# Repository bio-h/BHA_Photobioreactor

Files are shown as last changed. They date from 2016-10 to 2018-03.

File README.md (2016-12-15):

#BHA Photobioreactor

This project is still in alpha phase, meaning that the prototype is not functional at all.

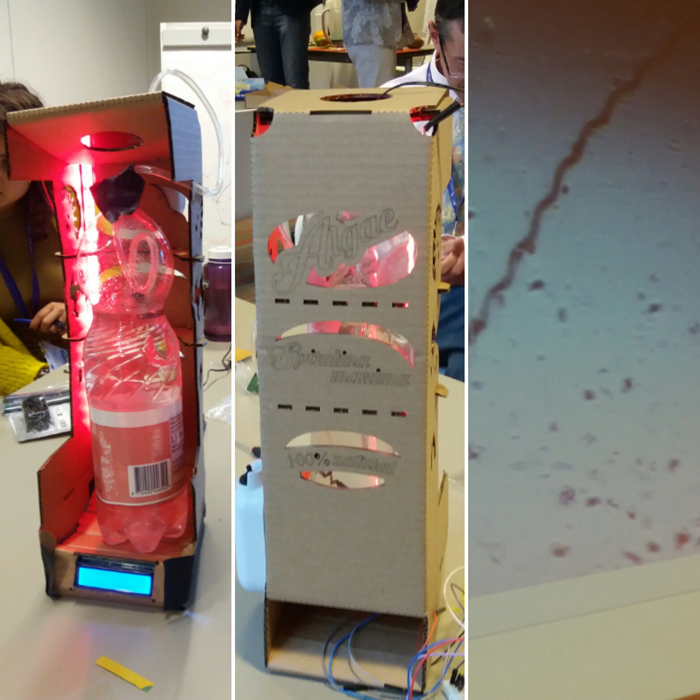
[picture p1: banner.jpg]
DIY Photobioreactor


The first release contains the source files of the designs and materials used during the #FOOD2030EU event in Brussels on Oct 12, 2016. The goal of that workshop was to prototype a device and have a discussion on bottom-up citizens led protein production. We built our own alpha version of the photobioreactor with the aim to grow Spirulina.

The goal of the Photobioreactor is to control or monitor the following parameters:

* Amount of light based on a day / night cycle
* Measure the amount of light
* Measure the pH
* Measure the temperature
* Display these values on an LCD screen

Follow these links for more information on [Spirulina](http://biohackacademy.github.io/bha3/annex/culture-collection/spirulina-maxima/) and its preferred [growth medium](http://biohackacademy.github.io/bha3/annex/cultivation-media/spirulina-medium/).

Here is a [video of a fully completed device](https://www.instagram.com/p/BLeMfMBlUFr/?taken-by=pvanboheemen).

<blockquote class="instagram-media" data-instgrm-captioned data-instgrm-version="7" style=" background:#FFF; border:0; border-radius:3px; box-shadow:0 0 1px 0 rgba(0,0,0,0.5),0 1px 10px 0 rgba(0,0,0,0.15); margin: 1px; max-width:658px; padding:0; width:99.375%; width:-webkit-calc(100% - 2px); width:calc(100% - 2px);"><div style="padding:8px;"> <div style=" background:#F8F8F8; line-height:0; margin-top:40px; padding:50.0% 0; text-align:center; width:100%;"> </div> <p style=" margin:8px 0 0 0; padding:0 4px;"> <a href="https://www.instagram.com/p/BLeMfMBlUFr/" style=" color:#000; font-family:Arial,sans-serif; font-size:14px; font-style:normal; font-weight:normal; line-height:17px; text-decoration:none; word-wrap:break-word;" target="_blank">Done! Spirulina #algea bioreactors build @Food2030EU prototyping how to grow your own protein</a></p> <p style=" color:#c9c8cd; font-family:Arial,sans-serif; font-size:14px; line-height:17px; margin-bottom:0; margin-top:8px; overflow:hidden; padding:8px 0 7px; text-align:center; text-overflow:ellipsis; white-space:nowrap;">A video posted by @pvanboheemen on <time style=" font-family:Arial,sans-serif; font-size:14px; line-height:17px;" datetime="2016-10-12T17:47:55+00:00">Oct 12, 2016 at 10:47am PDT</time></p></div></blockquote> <script async defer src="//platform.instagram.com/en_US/embeds.js"></script>

##Navigation the repo

 	BHA_Photobioreactor/						main repo
 	|-- Arduino/PhotobioreactorController/		Arduino Code
 	|-- Pictures/								Pictures of the device
 	BoM											Bill of Materials
 	Photobioreactor - Breadboard-wiring.png		Wiring overview
 	Photobioreactor - Electronics Assembly Guide.pdf		Assembly guide
 	Photobioreactor - Fritzing.fzz				Wiring source
 	Photobioreactor - Lasercut file.dxf			Laser cut sheet

Special thanks to: #FOOD2030EU @TogetherSci @waag #PolicyLabEU @EU_ScienceHub

## License

All code is licensed under GNU General Public License.

All designs are licensed under Creative Commons Contribution Share-Alike license

Copyright Waag Society

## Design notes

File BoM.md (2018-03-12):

## Bill of Materials

In this design we use the Arduino Leonardo microcontroller. These are abundantly available on the web, for example at [Bens Electronics](https://benselectronics.nl/arduino-leonardo/)(12.00)

### Components

These are the parts you will need to assemble the photobioreactor:

|No|Amount|Description|Supplier NL|Cost|
| ------------: | ------------: | :------------ | :------------ | ------------: |
|1|1|Big sheet of cardboard, just use an old box|-|-|
|2|1|Water proof temperature sensor NTC|[HackerStore](http://www.hackerstore.nl/Artikel/298), [Prototype Shop](http://www.prototypeshop.nl/temperatuursensor-waterdicht-ntc-10k-b3950-met-bevestigingsoog), [Adafruit](https://www.adafruit.com/product/372)|2.95|
|3|1|10K resistor|[Farnell](http://nl.farnell.com/te-connectivity/cfr16j10k/resistor-carbon-10k-0-25w-5/dp/2329474), [EOO](http://www.eoo-bv.nl/index.php?_a=viewProd&productId=7016)|0.06|
|4|1|I2C LCD display|[Bens Electronics](https://benselectronics.nl/16-x-2-hd44780-lcd-+-i2c-adapter-module/), [HackerStore](http://www.hackerstore.nl/Artikel/82), [iPrototype](https://iprototype.nl/products/components/led-lcd/lcd16x2-I2C-BL), [Hackerstore](https://www.hackerstore.nl/Artikel/82)|5.95|
|5|1|Digital Lux sensor (*1)|[HobbyElectronica](https://www.hobbyelectronica.nl/product/tsl2561-digitale-lux-licht-sensor/)|7.95|
|6|1|Digital lux sensor (*1)|[Bens Electronics](https://benselectronics.nl/gy302-bh1750-licht-intensiteit-sensor/)|3.50|
|7|1|Backflow valve|[Vijverbenodigdheden](https://www.vijverbenodigdheden.nl/tussenklep-terugslagklep-4-mm)|0.75|
|8|1|pH sensor|[iPrototype](https://www.iprototype.nl/products/components/sensors/analog-ph-meter-kit)|33.95|
|9|1|Relay|[Hobby Electronica](https://www.hobbyelectronica.nl/product/relais-module-2-kanaals-5v/)|2.95|
|10|1|Breadboard|[Bens Electronics](https://benselectronics.nl/breadboard-400-points/), [HackerStore](http://www.hackerstore.nl/Artikel/50)|3.00|
|11|2|Jumpwires|[Bens Electronics](https://benselectronics.nl/dupont-20cm-male-male/), [HackerStore](http://www.hackerstore.nl/Artikel/472)|0.75|
|12|2|Male-female wires|[Bens Electronics](https://benselectronics.nl/dupont-20cm-male-female/), [HackerStore](http://www.hackerstore.nl/Artikel/222)|0.75|
|13|1|Air pump|[Raven Hengelsport](https://www.raven.nl/raven-luchtpomp/nl/product/43517/)|8.99|
|14|1|Battery Alkaline C|[Albert Heijn](http://www.ah.nl/producten/product/wi136833/ah-alkaline-c-batterijen)|1.00|
|15|1|LED strip|[eBay](http://www.ebay.com/itm/401053939785)|2.90|
|16|1|7.5 W power supply|[iPrototype](https://iprototype.nl/products/accessoires/power/adapter), [EOO](http://www.eoo-bv.nl/index.php?_a=viewProd&productId=11642)|12.50|
|17|1|Spirulina culture|[eBay](http://www.ebay.com/itm/SPIRULINA-MAXIMA-STARTER-LIVE-100-ml-/172332270124?hash=item281fcdc22c:g:AfcAAOxygPtSzpv9)|15.00|

(*1) You may choose which light sensor you prefer 

The provided links are mere suggestions, there are cheaper sources such as eBay and Taobao.

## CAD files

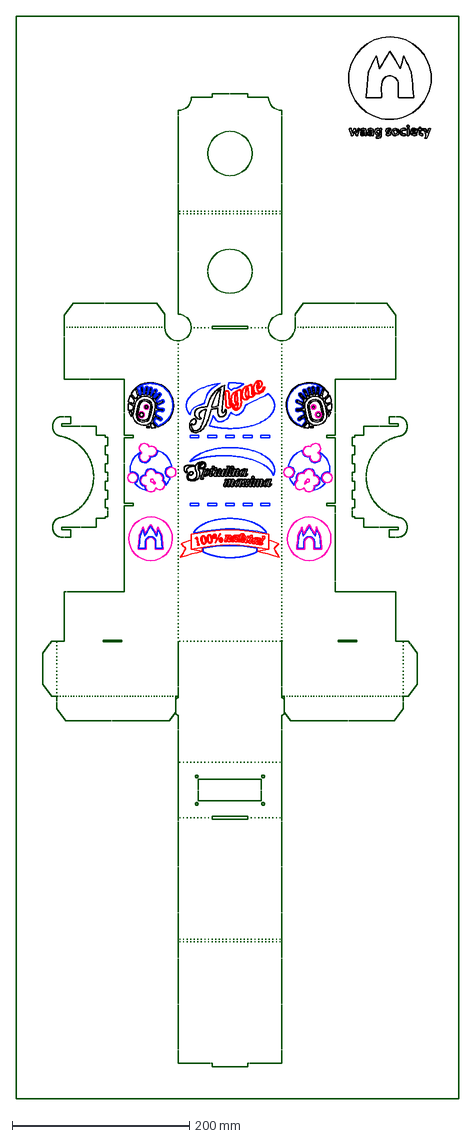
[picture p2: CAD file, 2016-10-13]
Photobioreactor - Lusercut file.dxf
500.0 x 1221.8 mm

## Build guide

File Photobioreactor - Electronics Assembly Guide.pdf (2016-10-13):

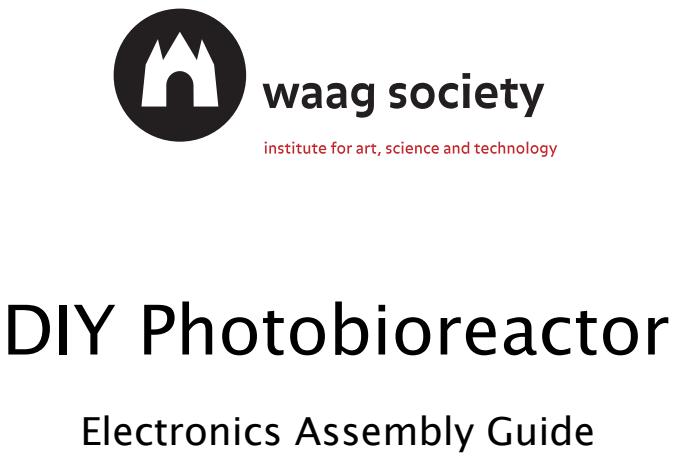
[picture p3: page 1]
DIY Photobioreactor

Electronics Assembly Guide

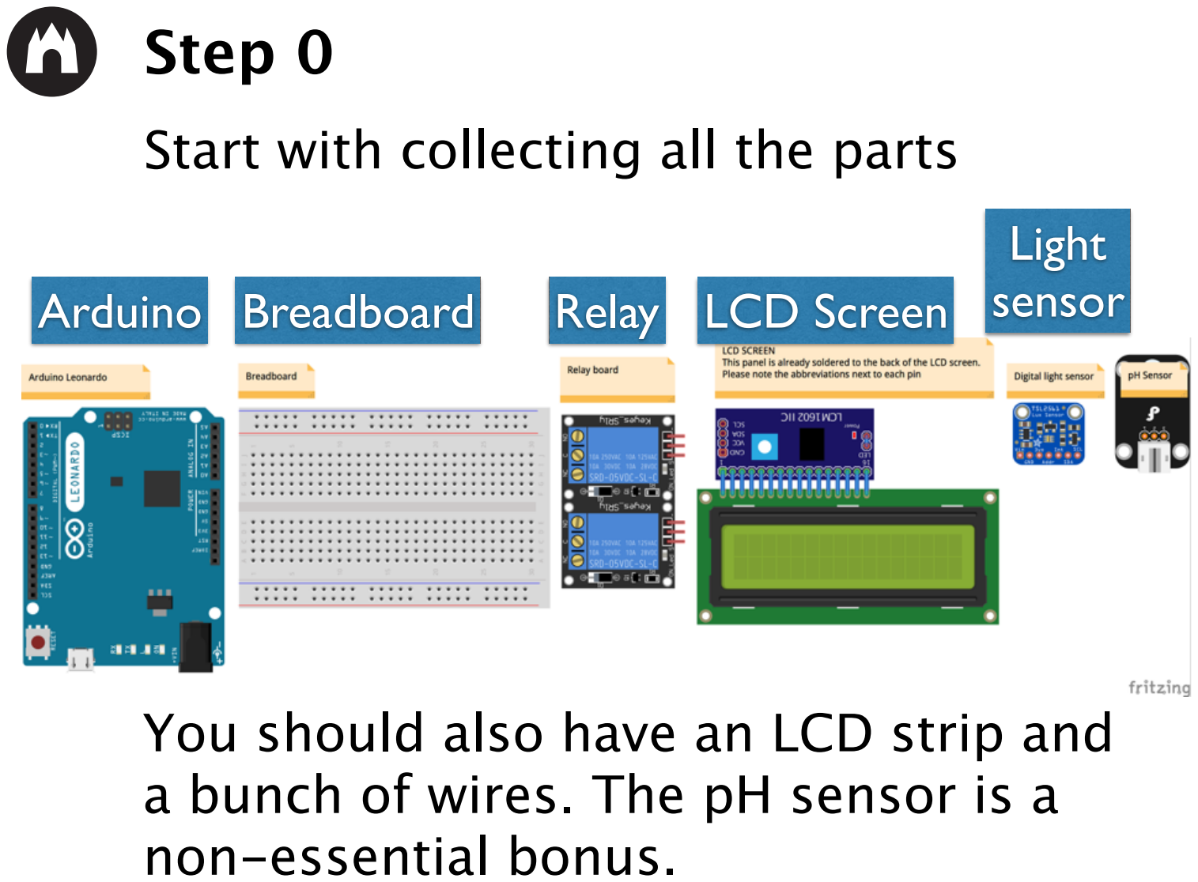
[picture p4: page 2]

Step 0
Start with collecting all the parts
Arduino | Breadboard | Relay | LCD Screen

Light
sensor

You should also have an LCD strip and a bunch of wires. The pH sensor is a non-essential bonus.

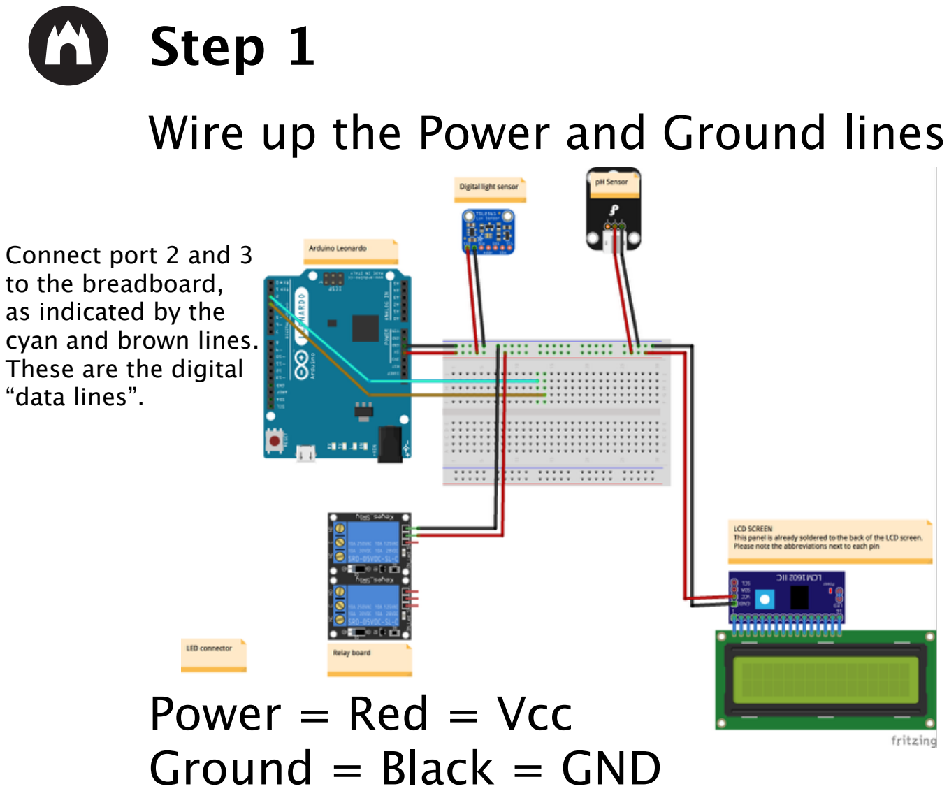
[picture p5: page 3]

Step 1
Wire up the Power and Ground lines

Power = Red = Vcc
Ground = Black = GND

Connect port 2 and 3
to the breadboard,
as indicated by the
cyan and brown lines.
These are the digital
“data lines”.

Step 2
Connect the light sensor to the data lines

Data = SDA = Cyan
Clock = SCL = Brown

Step 3
Connect the LCD to the data lines

Data = SDA = Cyan
Clock = SCL = Brown

Step 4 (Bonus step)
Connect the pH sensor

Signal = Orange

The signal from the
pH sensor must be
connected to Arduino
port A0

Step 5
Connect the temperature sensor

Signal = Green

The signal from the
temp sensor must be
connected to Arduino
port A1

Plug one side of the resistor
and one side of the temp sensor in the same column on the
breadboard. The signal wire must be connected to the same column. The other end of the resistor is connected to ground and the other end of the temp sensor to power.

Step 6
Connect the LED strip to the relay

Digital signal = Purple
12V Power = Banded Red = Vin (arduino)

Connect the LED strip
ground to GND port
on the Arduino.
And the LED strip
Vcc to the Relay

Power it up
Connect the 12V adapter to the Arduino

Arduino power
input jack

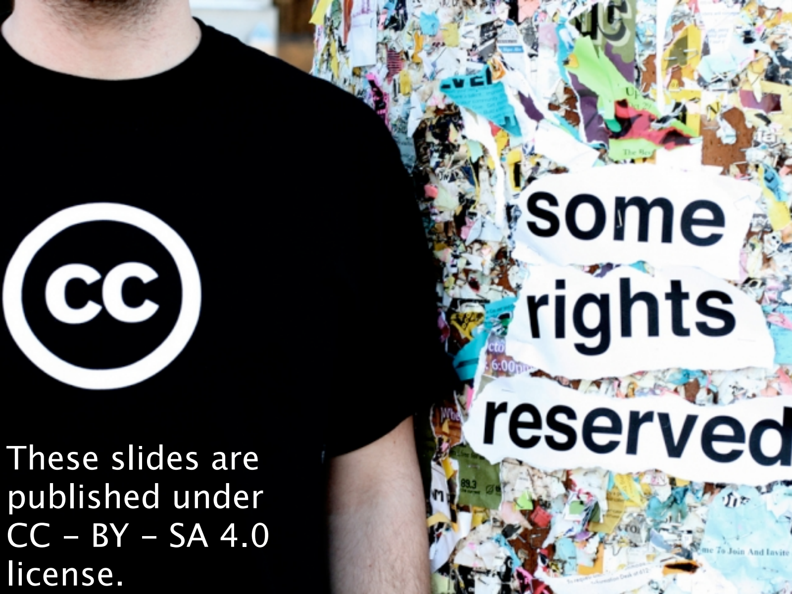
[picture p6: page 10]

These slides are
published under
CC - BY - SA 4.0
license.

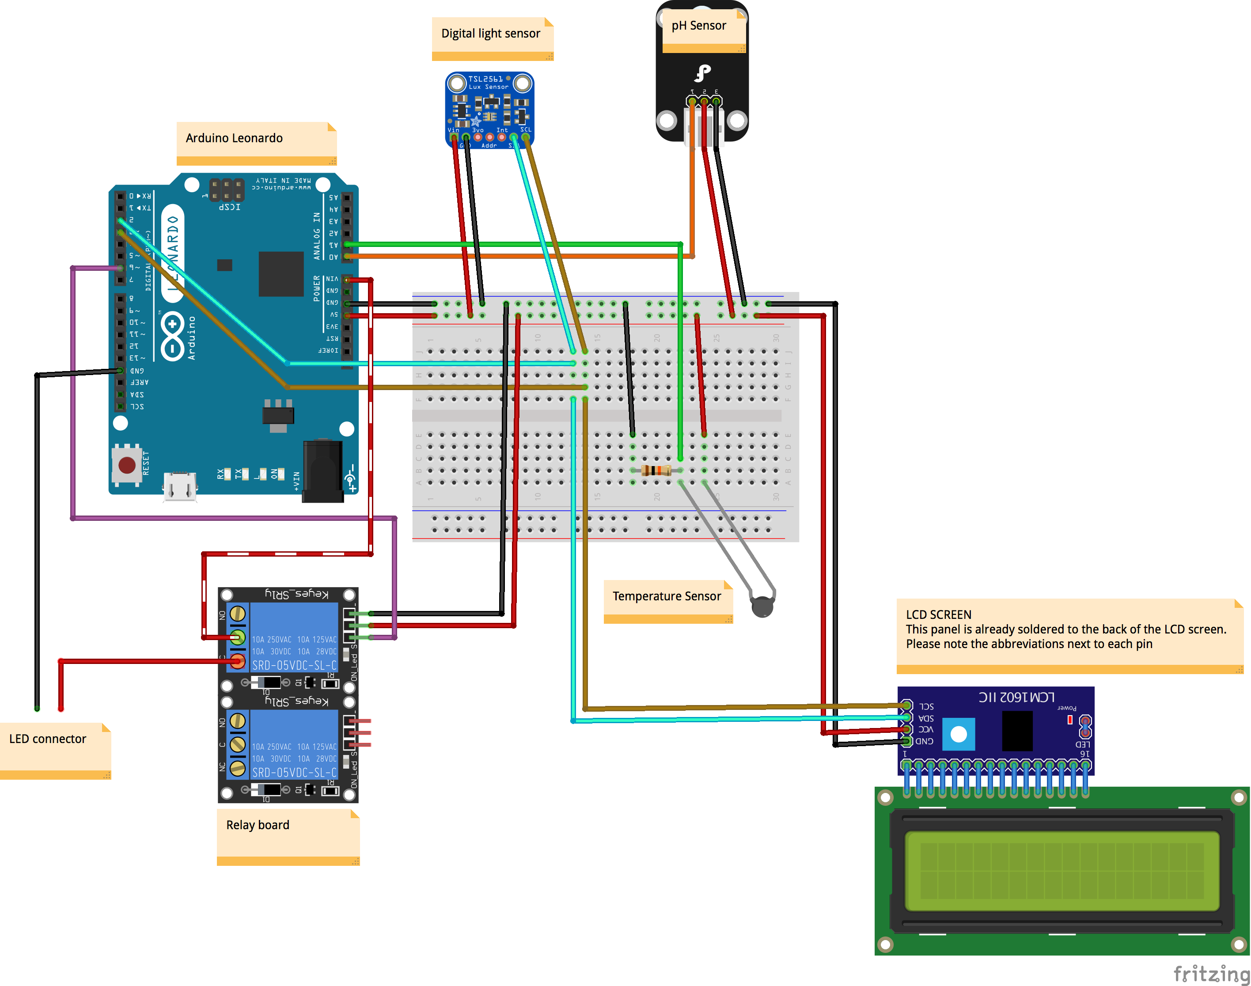
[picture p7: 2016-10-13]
Photobioreactor - Breadboard-wiring.png

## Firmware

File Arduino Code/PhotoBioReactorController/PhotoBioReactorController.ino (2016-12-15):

/*
	This file is part of Waag Society's Open Wetlab code repository

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
	You should have received a copy of the GNU General Public License
	along with this code. If not, see 
	<http://www.gnu.org/licenses/>.


# Instructions

The code includes a section on keeping track of time.
To synchronize the clock on Mac / Linux: you can use this command 
"date +T%s\n > /dev/ttyACM0" (UTC time zone)

You can modify the following settings:
- boolean lightSensorToggle = true;
  Choose between Adafruit (true) or BH1750 (false) light sensor
- int minhour = 8;
  int maxhour = 10;
  Set the hours of the day in between which the lights will be on
*/

/* *******************************************************
/  Libraries
*/
#include <Wire.h>
#include "LiquidCrystal_I2C.h" // Needed for operating the LCD screen
#include <math.h>
#include <Adafruit_Sensor.h>
#include <Adafruit_TSL2561_U.h>
#include <TimeLib.h>
#include <BH1750.h>
/* *******************************************************
*/

/* *******************************************************
/  Temperature calculation function
*/
double Thermistor(int RawADC) {
 double Temp;
 Temp = log(10000.0*((1024.0/RawADC-1))); 
 Temp = 1 / (0.001129148 + (0.000234125 + (0.0000000876741 * Temp * Temp ))* Temp );
 Temp = Temp - 273.15;            // Convert Kelvin to Celcius
 return Temp;
}

/* *******************************************************
/  pH sensor variables
*/
#define SensorPin 0          //pH meter Analog output to Arduino Analog Input 0
unsigned long int avgValue;  //Store the average value of the sensor feedback
float b;
int buf[10],temp;

/* *******************************************************
/  LCD
*/
// Set the LCD address to 0x27 for a 16 chars and 2 line display
LiquidCrystal_I2C lcd(0x27,16,2);
/* *******************************************************
*/

/* *******************************************************
/  Light sensor setup
*/
Adafruit_TSL2561_Unified tsl = Adafruit_TSL2561_Unified(TSL2561_ADDR_FLOAT, 12345);
BH1750 lightMeter;
boolean lightSensorToggle = true; // true = TSL2561, false = BH1750

/* *******************************************************
/  Clock variables
*/
#define TIME_HEADER  "T"   // Header tag for serial time sync message
#define TIME_REQUEST  7    // ASCII bell character requests a time sync message 
boolean LEDtoggle = true;
int minhour = 8;
int maxhour = 10;

/* *******************************************************
/  Configures the gain and integration time for the TSL2561
*/
void configureSensor(void)
{
  /* You can also manually set the gain or enable auto-gain support */
  // tsl.setGain(TSL2561_GAIN_1X);      /* No gain ... use in bright light to avoid sensor saturation */
  // tsl.setGain(TSL2561_GAIN_16X);     /* 16x gain ... use in low light to boost sensitivity */
  tsl.enableAutoRange(true);            /* Auto-gain ... switches automatically between 1x and 16x */
  
  /* Changing the integration time gives you better sensor resolution (402ms = 16-bit data) */
  tsl.setIntegrationTime(TSL2561_INTEGRATIONTIME_13MS);      /* fast but low resolution */
  // tsl.setIntegrationTime(TSL2561_INTEGRATIONTIME_101MS);  /* medium resolution and speed   */
  // tsl.setIntegrationTime(TSL2561_INTEGRATIONTIME_402MS);  /* 16-bit data but slowest conversions */

  /* Update these values depending on what you've set above! */  
  Serial.println("------------------------------------");
  Serial.print  ("Gain:         "); Serial.println("Auto");
  Serial.print  ("Timing:       "); Serial.println("13 ms");
  Serial.println("------------------------------------");
}

/* *******************************************************
/  Setup function, this code only runs once
*/
void setup()
{
  /* Open Serial connection */
  Serial.begin(9600);  
  Serial.println("Ready");    //Test the serial monitor

  /* Set LED pin to output */
  pinMode(13,OUTPUT); 
  pinMode(6,OUTPUT);

  if(lightSensorToggle) {
    /* Initialise the Adafruit light sensor */
    if(!tsl.begin())
    {
      /* There was a problem detecting the ADXL345 ... check your connections */
      Serial.print("Ooops, no TSL2561 detected ... Check your wiring or I2C ADDR!");
      while(1);
    }
    
    /* Setup the sensor gain and integration time of the light sensor */
    configureSensor();
  }
  else {
    /* Initialise the BH1750 ligth sensor */
    lightMeter.begin();
  }
  
  /* Setup the clock */
  setSyncProvider( requestSync);  //set function to call when sync required

  // Initialize the LCD and print a message
  lcd.init(); // start the LCD
  lcd.backlight(); // enable the backlight
  lcd.clear(); // Clear the screen from any character
  lcd.setCursor(0,0); // Start writing from position 0 row 0, so top left
  lcd.print("Photobioreactor");
  delay(1000);
  lcd.clear();

}

/* *******************************************************
/* Loop, this code is continiously repeated
*/
void loop()
{
  /* Process clock sync message */
  if (Serial.available()) {
    processSyncMessage();
  }
  if (timeStatus()!= timeNotSet) {
    digitalClockDisplay();  
  }
  if(hour()>minhour && hour()<maxhour) {
    digitalWrite(6, HIGH);
    LEDtoggle = true;
  }
  else {
    digitalWrite(6, LOW);
    LEDtoggle = false;
  }
  
  /* pH sensor reading */
  for(int i=0;i<10;i++)       //Get 10 sample value from the sensor for smooth the value
  { 
    buf[i]=analogRead(SensorPin);
    delay(10);
  }
  for(int i=0;i<9;i++)        //sort the analog from small to large
  {
    for(int j=i+1;j<10;j++)
    {
      if(buf[i]>buf[j])
      {
        temp=buf[i];
        buf[i]=buf[j];
        buf[j]=temp;
      }
    }
  }
  avgValue=0;
  for(int i=2;i<8;i++)                      //take the average value of 6 center sample
    avgValue+=buf[i];
  float phValue=(float)avgValue*5.0/1024/6; //convert the analog into millivolt
  phValue=3.5*phValue;                      //convert the millivolt into pH value
  Serial.print("    pH:");  
  Serial.print(phValue,2);
  Serial.println(" ");

  sensors_event_t event;

  if(lightSensorToggle) {
    /* Adafruit light sensor reading */
    
    tsl.getEvent(&event);
   
    /* Display the Adafruit light sensor results (light is measured in lux) */
    if (event.light)
    {
      Serial.print(event.light); Serial.println(" lux");
    }
  }
  else {
    /* BH1750 light sensor */
    uint16_t lux = lightMeter.readLightLevel();
    Serial.print("Light: ");
    Serial.print(lux);
    Serial.println(" lux");
  }
  
  /* Temperature sensor reading */
  Serial.println(int(Thermistor(analogRead(1))));
  
  /* LCD display output */
  lcd.clear();
  lcd.setCursor(0,0);
  lcd.print("Temp:");
  lcd.print(int(Thermistor(analogRead(1))));
  lcd.print(" ");
  lcd.print(hour());
  printLCDDigits(minute());
  lcd.print(" ");
  if(LEDtoggle) {
    lcd.print("*");
  } else {
    lcd.print("-");
  }
  lcd.setCursor(0,1);
  lcd.print("pH:");  
  lcd.print(int(phValue));
  lcd.print(" Lux:");
  if(lightSensorToggle) { 
    lcd.print(int(event.light)); // Adafruit
  }
  else {
    uint16_t lux = lightMeter.readLightLevel();
    lcd.print(int(lux)); // BH1750
  }
  
  /* Blink LED as status indicator */
  digitalWrite(13, HIGH);       
  delay(800);
  digitalWrite(13, LOW); 
}






/* Functions for setting the clock */
void digitalClockDisplay(){
  // digital clock display of the time
  Serial.print(hour());
  printDigits(minute());
  Serial.print(" ");
  Serial.print(day());
  Serial.print(" ");
  Serial.print(month());
  Serial.print(" ");
  Serial.print(year()); 
  Serial.println(); 
}

void printDigits(int digits){
  // utility function for digital clock display: prints preceding colon and leading 0
  Serial.print(":");
  if(digits < 10)
    Serial.print('0');
  Serial.print(digits);
}

void printLCDDigits(int digits){
  // utility function for digital clock display: prints preceding colon and leading 0
  lcd.print(":");
  if(digits < 10)
    lcd.print('0');
  lcd.print(digits);
}

void processSyncMessage() {
  unsigned long pctime;
  const unsigned long DEFAULT_TIME = 1357041600; // Jan 1 2013

  if(Serial.find(TIME_HEADER)) {
     pctime = Serial.parseInt();
     if( pctime >= DEFAULT_TIME) { // check the integer is a valid time (greater than Jan 1 2013)
       setTime(pctime); // Sync Arduino clock to the time received on the serial port
     }
  }
}

time_t requestSync()
{
  Serial.write(TIME_REQUEST);  
  return 0; // the time will be sent later in response to serial mesg
}

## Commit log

2016-10-13 Source codes
    [Photobioreactor-Fritizing.fzz]
2016-12-15 BHA4 update
    [Photobioreactor - Fritzing.fzz]
2017-02-21 update schematic in .fzz
    [Photobioreactor - Fritzing.fzz]

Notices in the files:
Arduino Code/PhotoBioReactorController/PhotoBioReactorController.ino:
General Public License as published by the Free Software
